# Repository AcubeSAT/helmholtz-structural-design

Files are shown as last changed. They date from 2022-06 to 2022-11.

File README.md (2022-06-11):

## **Hello, Helmholtz enthusiasts!**

This readme is for people who don't want to or don't know how to use a 3D CAD software.
*Click each of the following links to be redirected to a page where you can see the 3D design sub-assemblies and the whole assembly.*

Helmholtz assembly:
https://autode.sk/3tvBUBP

Frame:
https://autode.sk/3QcUYyy

Coil corner:
https://autode.sk/3QebGxv

All 3 coil assemblies are similar with different dimensions. Here is the middle one:
https://autode.sk/3Ha60Ay

Bracket for X and Y coils mounting:
https://autode.sk/3QhkKli

Bracket for Z coils mounting:
https://autode.sk/3NKaX5m

Helmholtz_Cage

Frame

Coil

## Have fun!

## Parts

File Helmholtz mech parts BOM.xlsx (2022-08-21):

Subassembly | No | Name | Details | Quantity | Comments
F | 1 | Vertical Beams | T-slot 20x20 aluminum profile | Length 2000mm | 4 | Procured, measured, are fine
 | 2 | Z coils supports | T-slot 20x20 aluminum profile | Length 1790mm | 4 | Procured, measured, are fine
 | 3 | ±X table supports | T-slot 20x20 aluminum profile | Length 840mm | 2 | Procured, measured, are fine
 | 4 | ±Υ table supports | T-slot 20x20 aluminum profile | Length 810mm | 2 | Procured, measured, are fine
 | 5 | X coils supports | T-slot 20x40 aluminum profile | Length 840mm | 4 | Procured, measured, are fine
 | 6 | Y coils supports | T-slot 20x40 aluminum profile | Length 810mm | 4 | Procured, measured, are fine
 | 7 | Testing table | Aluminum sheet 2x840x810mm | 1 | Not procured yet
 | 8 | Double profile brackets | 20x40 aluminum brackets (4 bolt holes) | 16 | Procured, assemblable
 | 9 | Square profile brackets | 20x20 aluminum brackets (2 bolt holes) | 16 | Procured, assemblable
 | 10 | M5 stainless steel bolts |  | 128 | Procured galvanized steel ones for assembly, reordered correct ones) dimension concern for length
 | 11 | M5 stainless steel nuts |  | 128 | Procured galvanized steel ones for assembly, reordered correct ones)
 | 12 | Z coils brackets |  | 8 | Not finished printing yet (need a small alteration)
 | 13 | X-Y coils brackets |  | 16 | Not finished printing yet
X Y Z | 14 | Corner ground parts | thickness 3mm | 24 | Procured, assembled
 | 15 | Corner side parts | thickness 2mm | 48 | Procured, assembled
Z | 16 | Z coil channels | Aluminum U-profile 20x50 length 1650mm | 8 | Procured, assembled
Y | 17 | Y coil channels | Aluminum U-profile 20x50 length 1600mm | 8 | Procured, assembled
X | 18 | X coil channels | Aluminum U-profile 20x50 length 1550mm | 8 | Procured, assembled
X Y Z | 19 | Rivets | Aluminum 4mm diameter | 192 | Procured, assembled

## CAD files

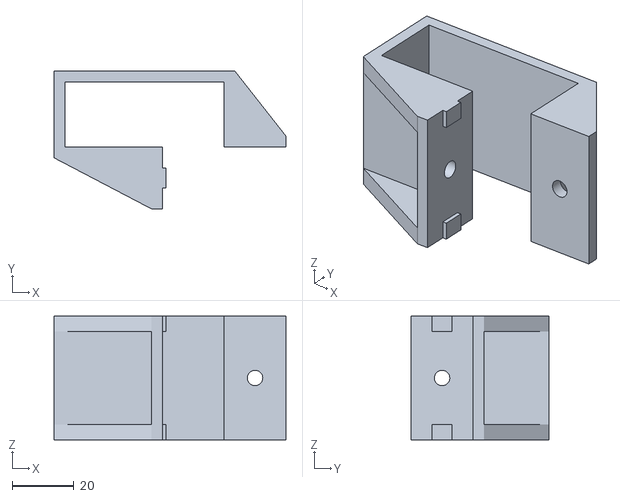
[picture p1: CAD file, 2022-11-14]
Helmholtz X-Y bracket (NEW 14-11-2022) (PITSOS - CHATZIARGIRIOU).STL
75.0 x 44.5 x 40.0

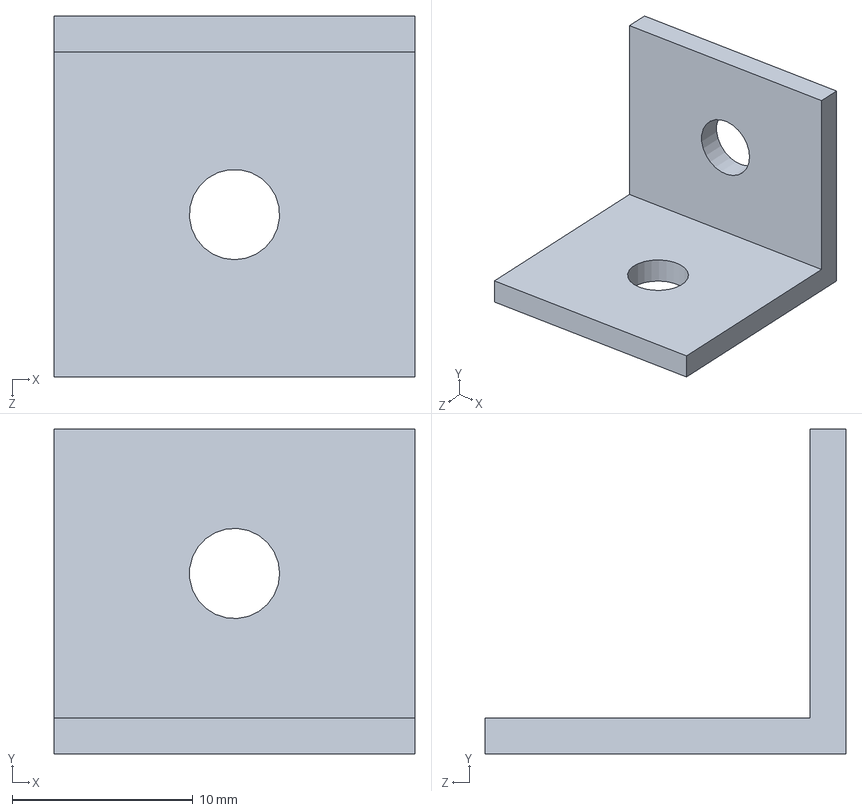
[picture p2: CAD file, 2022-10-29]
Support bracket (simple).SLDPRT
20.0 x 18.0 x 20.0 mm

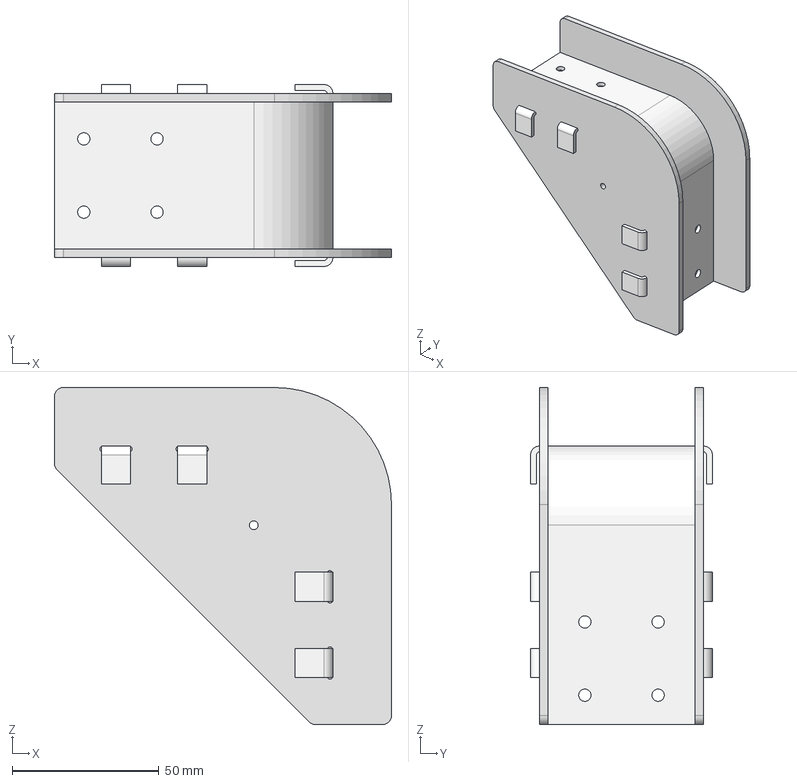
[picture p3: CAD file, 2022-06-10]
Corner v2.stp
115.0 x 62.0 x 115.0 mm
Corner side v2 x 2
Corner ground v2

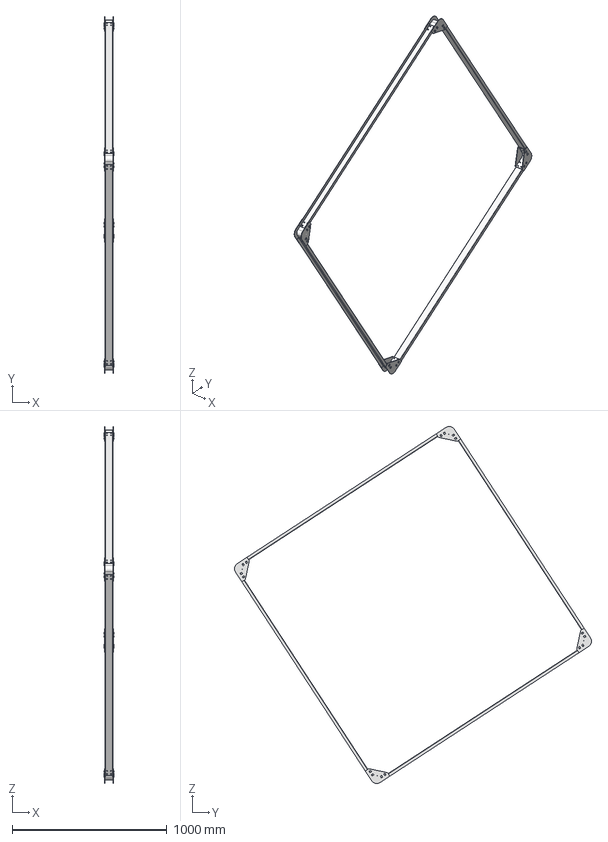
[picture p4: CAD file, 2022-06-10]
Inner coil v2.stp
62.0 x 2308.0 x 2308.0 mm
Inner channel x 4
Corner side v2 x 8
Corner ground v2 x 4
rivets x 32

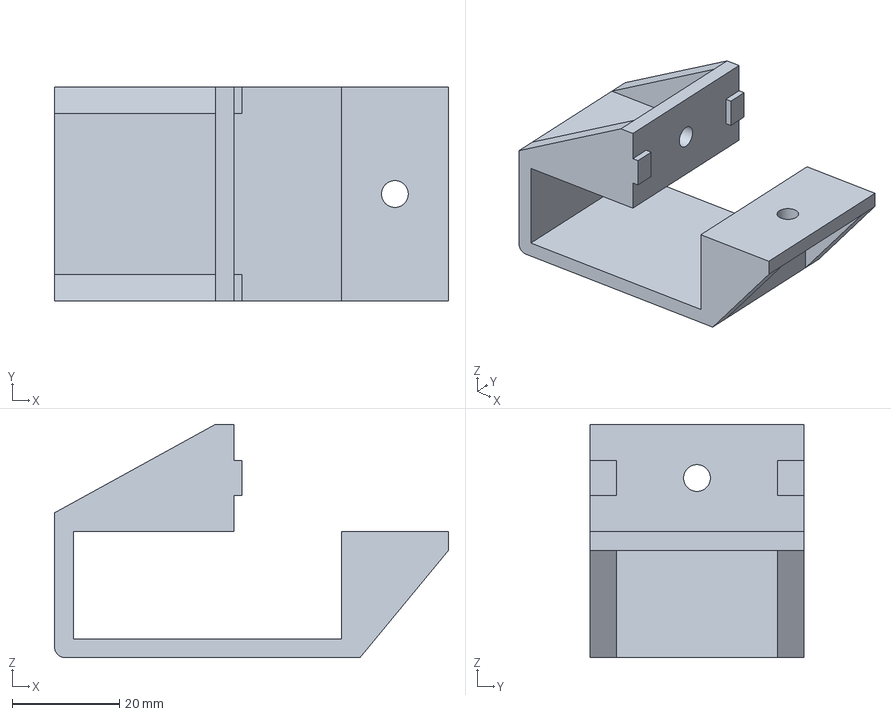
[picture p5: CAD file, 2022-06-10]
X-Y bracket.stp
73.5 x 40.0 x 43.5 mm

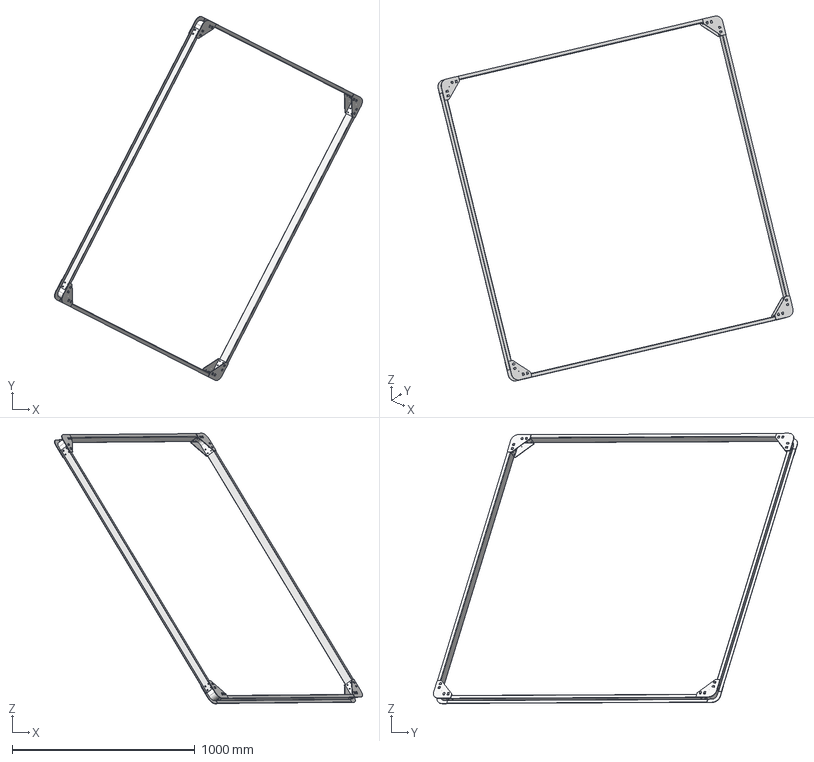
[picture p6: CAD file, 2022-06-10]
Middle coil v2.stp
1684.5 x 1991.8 x 1479.6 mm
Corner side v2 x 8
Corner ground v2 x 4
Middle channel x 4
rivets x 32

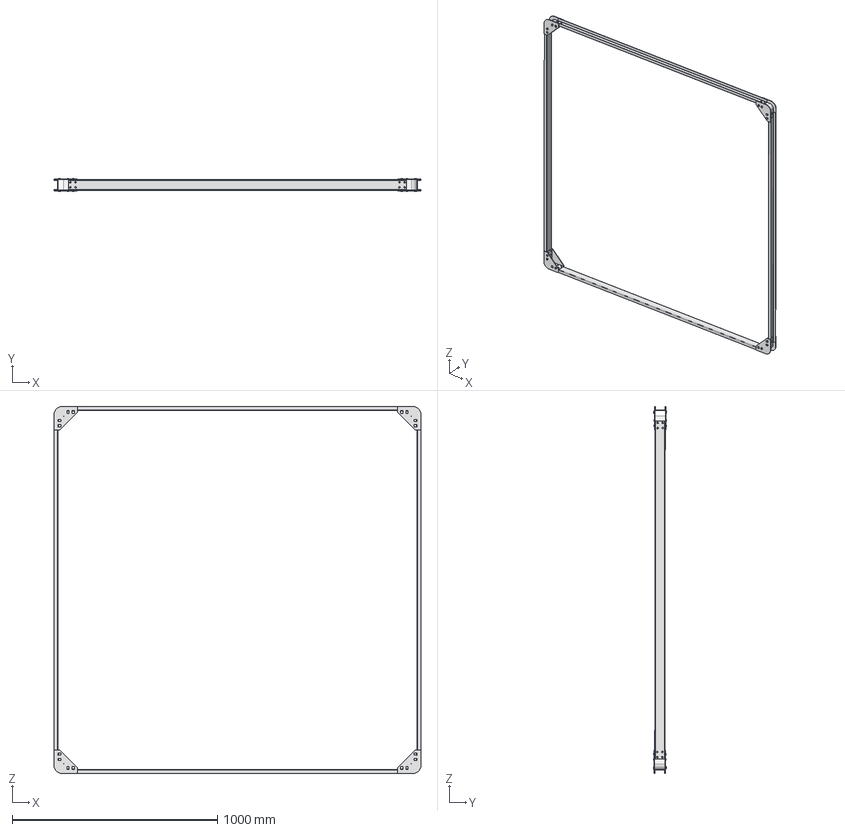
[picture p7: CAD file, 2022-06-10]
Outer coil v2.stp
1790.0 x 63.5 x 1790.0 mm
Corner side v2 x 8
Corner ground v2 x 4
Outer channel x 4
rivets x 32

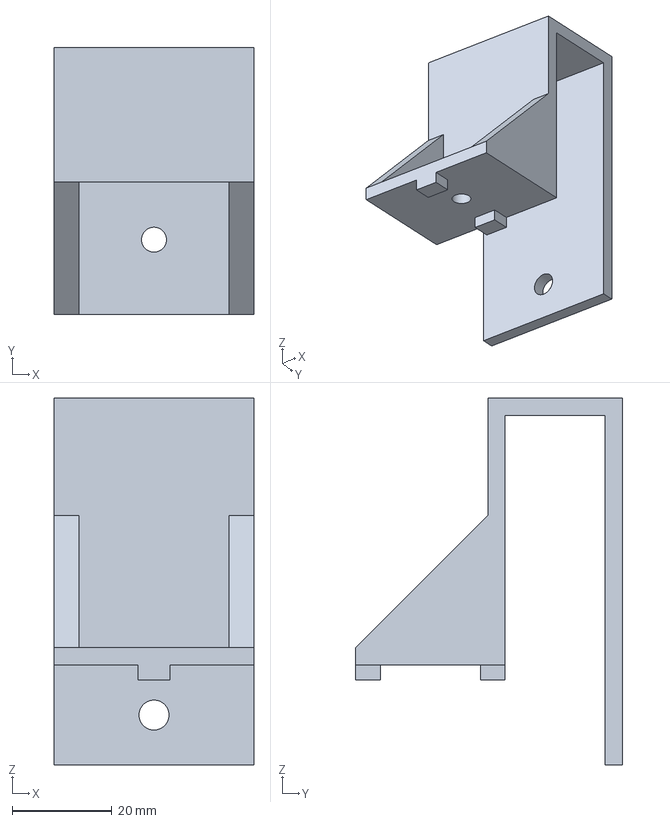
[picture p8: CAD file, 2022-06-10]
Z bracket.stp
40.0 x 53.5 x 73.5 mm

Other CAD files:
Mechanical drawings/Corner side v2.dwg
Mechanical drawings/Corner ground v2.dwg
Support bracket (simple).STL

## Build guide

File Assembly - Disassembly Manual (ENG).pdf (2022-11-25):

## BILL OF MATERIALS

1. 128 Μ5 stainless steel bolts
2. 128 Μ5 stainless steel nuts
3. 4 Vertical beams (T-slot 20x20 aluminum profile - Length 2000mm)
4. 4 Z coils beams (T-slot 20x20 aluminum profile - Length 1790mm)
5. 4 X coils beams (T-slot 20x40 aluminum profile - Length 840mm)
6. 4 Y coils beams (T-slot 20x40 aluminum profile - Length 810mm)
7. 1 Testing table (Aluminum sheet 2x840x810mm)
8. 2 ±X table beams (T-slot 20x20 aluminum profile - Length 840mm)
9. 2 ±Υ table beams (T-slot 20x20 aluminum profile - Length 810mm)
10. 16 Double profile brackets (20x40 aluminum brackets (4 bolt holes))
11. 16 Square profile brackets (20x20 aluminum brackets (2 bolt holes))
12. 8 Z coils brackets
13. 16 X-Y coils brackets
14. 2 X coils (side length 1650mm)
15. 2 Υ coils (side length 1700mm)
16. 2 Z coils (side length 1750mm)
17. 16 support brackets

For the assembler’s convenience, the following parts shall be renamed:
Item number, from BoM | Initial name, from BoM | Final name, referred as in document
3 | Vertical beams (T-slot 20x20 aluminum profile -Length 2000mm) | XL
4 | Z coils beams (T-slot 20x20 aluminum profile -Length 1790mm) | L
5 | X coils beams (T-slot 20x40 aluminum profile -Length 840mm) | x2/84
6 | Y coils beams (T-slot 20x40 aluminum profile -Length 810mm) | x2/81
8 | ±X table beams (T-slot 20x20 aluminum profile - Length 840mm) | TBL X
9 | ±Υ table beams (T-slot 20x20 aluminum profile - Length 810mm) | TBL Y
10 | Double profile brackets (20x40 aluminum brackets (4 bolt holes)) | Double brackets
11 | Square profile brackets (20x20 aluminum brackets (2 bolt holes)) | Single brackets

## PRELIMINARY WORK

Brackets preparation
We take a screw, pass it through a hole of our choice from a double bracket and screw a nut on the other side, making sure that the flat surface of the nut faces the double bracket. We repeat this procedure for all the double brackets, and work similarly for the single brackets. It is important that half of the double brackets have the screw in the left hole, and the other half have it in the right, like they are projections on a mirror.

Preparation of x2/84 and x2/81 supports
We assemble all the x2/84 and x2/81 supports. On the 40mm wide surface (big surface), and channel of our choice, we insert a double bracket with the blank back facing outwards and align the back of the double bracket with the edge of the support, then tighten the screw. We repeat the process on the other side of the support. CAUTION!!! At this point, the screws from the two double brackets should be in the same channel of the big surface of the x2/84 and x2/81 supports.

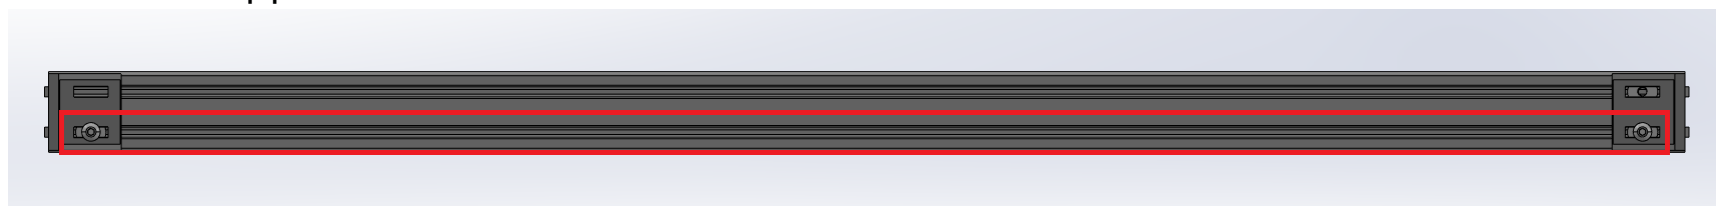
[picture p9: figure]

Preparation of the TBL X and TBL Y supports
We assemble all of the TBL X and TBL Y supports. Using the single brackets, we work similarly to the preparation of the x2/84 and x2/81 supports.

Preparation of the L supports
We assemble all the L supports. At a distance equal to 47.1cm from each side, we mark the point. For the input of a single bracket, we insert it in the channel with the back with the empty hole facing outside of the L support (at 90 degrees). We align the single bracket's flat surface, which is facing towards the side it was inserted from, with the 47,1cm mark and tighten the screw. We repeat this procedure for the other side of this L support. We repeat this procedure for all the L supoorts. CAUTION!!! The surface with the empty hole of all the single brackets must be facing the same way.

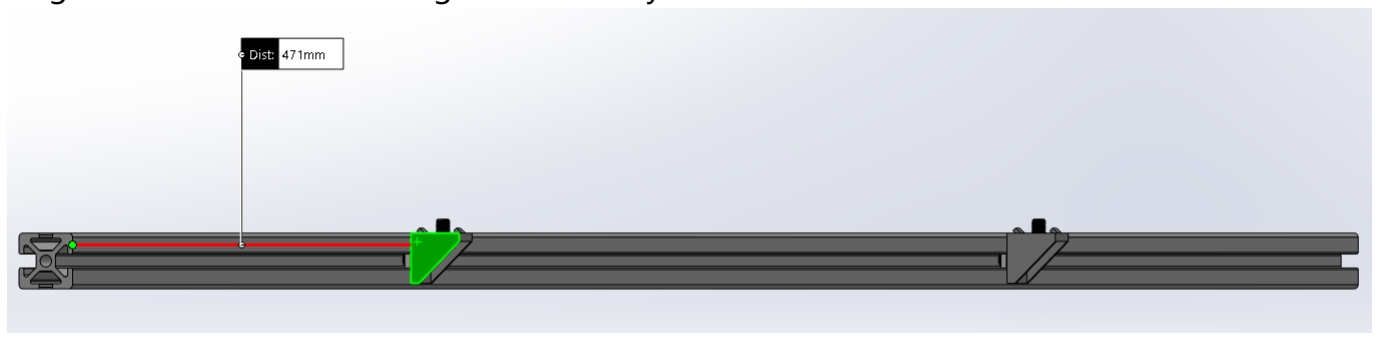
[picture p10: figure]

Figure 1. Single brackets distance and placing
At this point, the 4 L supports should have 8 single brackets mounted on them, in total, which will all be in the same channel, and the empty hole of all the single brackets will be facing the same way.

## ASSEMBLY

COALESCENCE OF THE 4 XL BEAMS
For the assembler's convenience, the bottom of the XL beams will be called the (-) side, whereas the top will be called the (+) side.

We take 2 XL beams and at a distance of 26cm from the bottom (-), we mark the spot. We take one x2/81 support and insert it in the channel of an XL beam with its blank side facing the top (+) of the cage, while the side which bears the double bracket faces the bottom (-). We align the blank surface with the 26cm mark, and tighten the screw. We repeat this process for the other XL beam. Finally, we repeat all the above steps with the other 2 XL beams and 1 x2/81 support. CAUTION!!! The protruding part of the x2/81 support MUST be towards the outside area of the cage.

At this point, we have joined together the 4 XL beams in pairs of 2.

Next, at a distance of 28.7cm from the bottom (-) of the XL beams, we mark the spot. Using one of the two pairs of XL beams, we insert a x2/84 bracket into the channel of an XL bracket with the blank surface facing the top (+) and the side with the double brackets facing the base (-). Align the blank surface with the 28.7cm mark, and tighten the screws to stabilize the support. We are now able to join the 2 pairs by inserting the other end of this x2/84 support into the channel of the other XL pair. Finally, we insert another x2/84 from the other side and work in a similar way to close the loop. CAUTION!!! At this point the 4 XL brackets should be joined together, and the side of x2/81 and x2/84 that protrudes from the frame should be OUTSIDE the cage.

At this point, the cage should look like this.

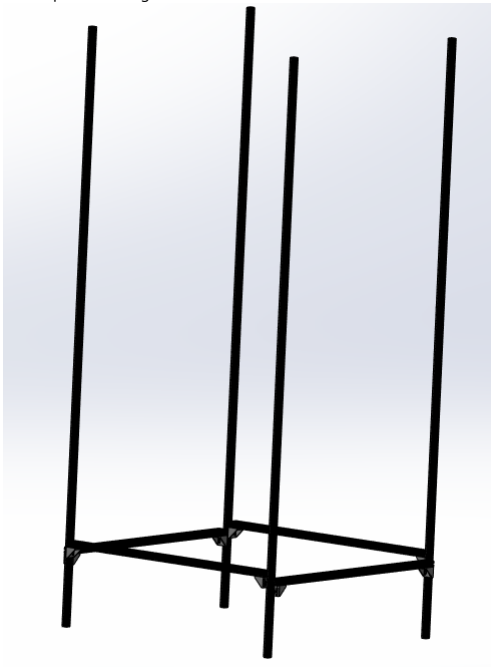
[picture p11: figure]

Figure 2. Coalescence of the XL supports

LOWER Z SUPPORTS PLACEMENT
At a distance equal to 60.9cm from the base (-) we mark the spot. The L supports MUST be inserted on the same sides as the x2/81 supports. The L supports MUST be facing the inside area of the cage. We align the blank surface with the 60.9cm mark, facing the top (+), and tighen the screw.

At this point, the cage should look like this.

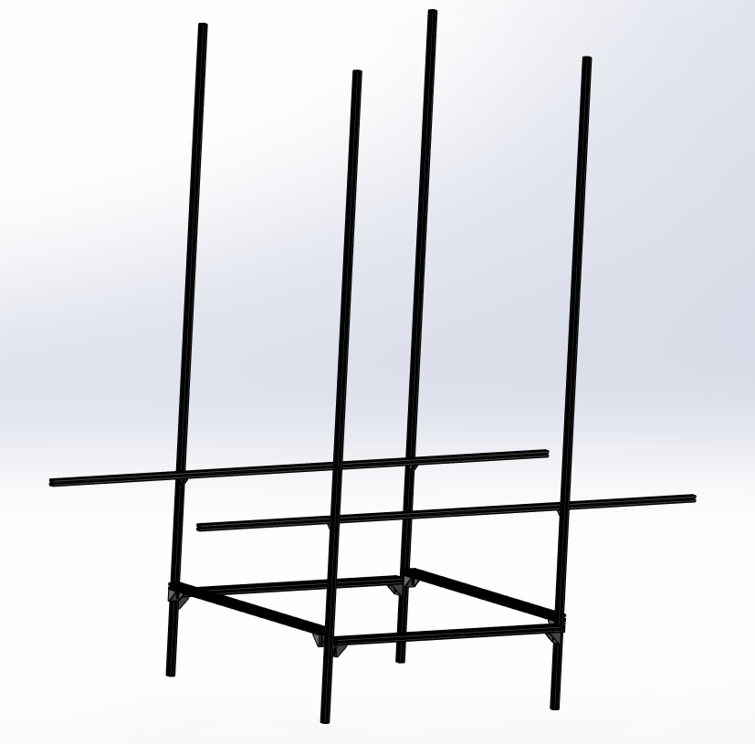
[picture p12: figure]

Figure 3. Lower Z supports
TABLE PLACEMENT
At a distance equal to 113cm from the base (-) we mark the spot.
To mount the TBL X supports, we insert them from the same sides as the x2/84 supports. To install the first TBL X, insert the bracket with the single bracket side facing the base (-). Align the blank surface of the TBL X with the 113cm mark, and tighten the screw. Repeat the procedure for the other TBL X support. In a similar way, we insert the TBL Y brackets from the sides of the x2/81 brackets, and repeat the procedure.

At this point, we have the 4 table brackets TBL X and TBL Y with their blank surface aligned with the 113cm mark, and with the single bracket facing the base (-). Also, the TBL X are parallel to the x2/84, while the TBL Y are parallel to the x2/81.

We place the table on top of its supports, with the longer side (840mm) on the TBL X supports and the shorter side (810mm) on the TBL Y supports.

At this point, the cage should look like this.

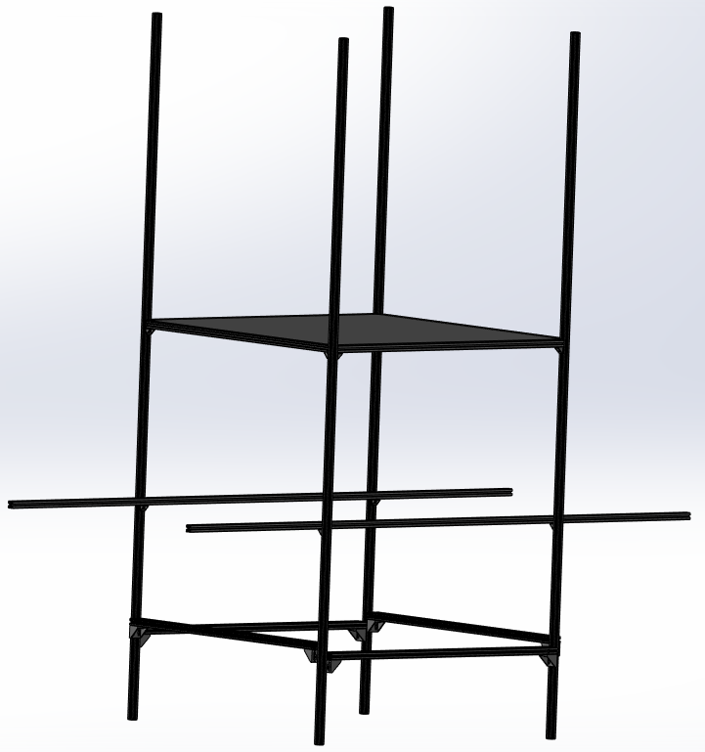
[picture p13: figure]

Figure 4. Table and its supports

UPPER Ζ SUPPORTS PLACEMENT
At a distance equal to 156.1cm from the base (-) we mark the spot. The L supports MUST be inserted on the same sides as the x2/81 and TBL Y supports. The L supports MUST be facing the inside area of the cage. We align the blank surface with the 156.1cm mark, facing the top (+), and tighen the screw.

At this point we have placed the 4 L supports, facing towards the inside are of the cage, and parallel to the x2/81 and TBL Y supports.

At this point, the cage should look like this.

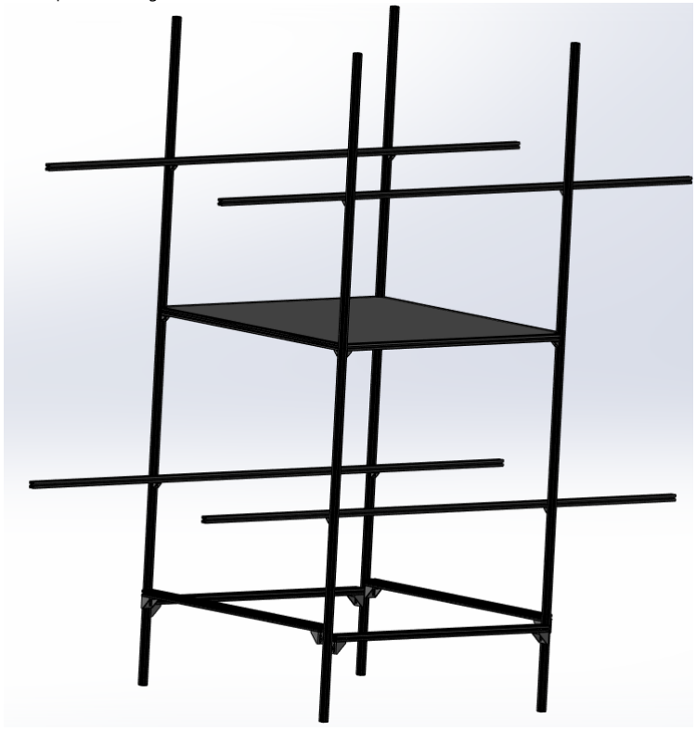
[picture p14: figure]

Figure 5. Upper Z supports

TOP SUPPORTS PLACEMENT
At a distance of 2cm and 4.35cm from the top (+), we mark the spot.

For the placement of the final 2 x2/81 supports, we insert them from the top (+) of the sides that have the other 2 x2/81 and TBL Y supports mounted. We insert them with the brackets facing towards the base (-), align the blank surface with the 2cm mark, and tighten the screws.

Similarly, we mount the final 2 x2/84 supports to the top (+) of the sides that have the other 2 x2/84 and TBL X supports. We align the blank surface with the 4.35cm mark, and tighten the bolts.

At this point, we have set up the main frame infrastructure, alongside all the internal supports. The cage should look like this.

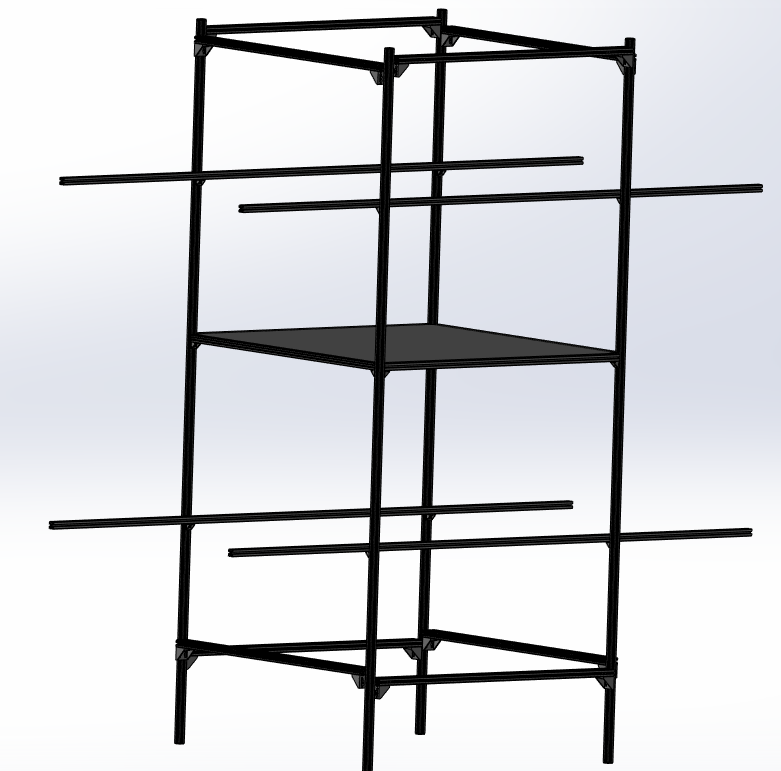
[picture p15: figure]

Figure 6. Top supports

COILS PLACEMENT
The first coils to be mounted are the X coils (side length 165cm) atop the x2/84 supports. Next, the Y coils are placed (side length 170cm) atop the x2/81 supports. During the Y coils' installation, we mount them outside of the X coils.

Finally, we place the Z coils (side length 175cm) outside of the other 2, and mount them atop the L supports.

At this point, the cage should look like this.

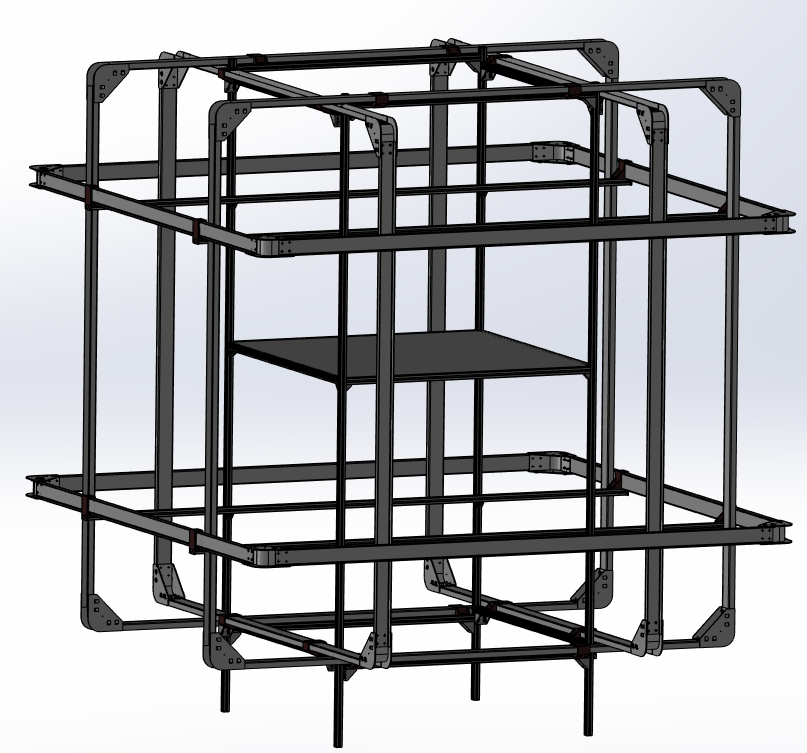
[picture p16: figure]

Figure 7. Assembled Helmholtz cage, with frame and coils

## SUPPORT BRACKETS

In order ot further improve the overall stability of the assembly, 3D printed brackets are being utilized.
There are 3 types of brackets:
- X-Y brackets for the X-Y coils
- Z brackets for the Z coils
- Support brackets for the x2/81 and x2/84 beams

The X-Y brackets keep the X and Y coils in place atop the x2/81 and x2/84 beams. There is no fixed position for them to be screwed. It's up to the assembler.

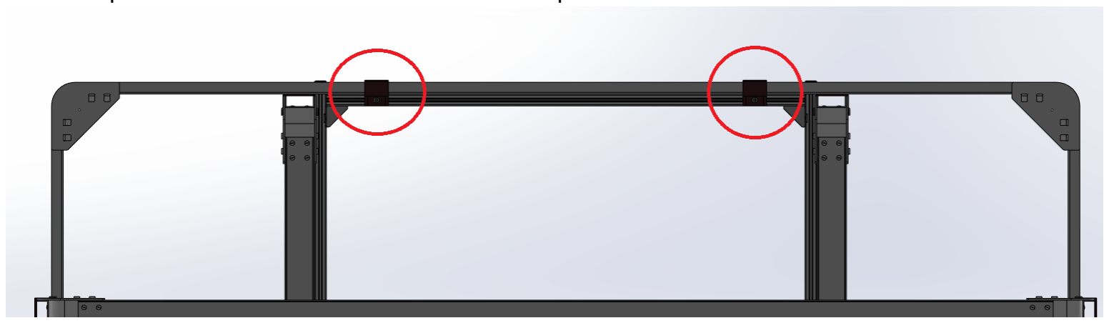
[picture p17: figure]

The Z brackets keep the Z coils in place at the edges of the L beams.
If the inside of the beam is threaded, an additional screw may be used to further stabilize the assembly.

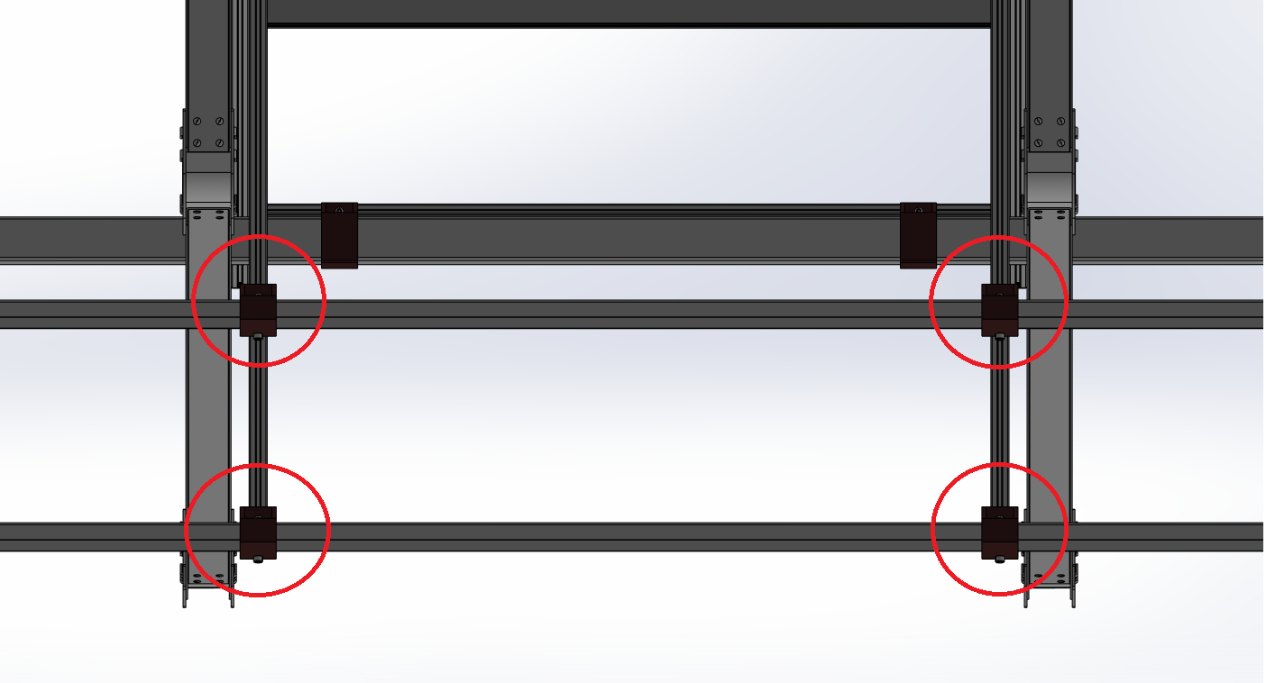
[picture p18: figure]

The support brackets further stabilize the x2/81 and x2/84 beams, keeping them from rotating due to the coils' weight.

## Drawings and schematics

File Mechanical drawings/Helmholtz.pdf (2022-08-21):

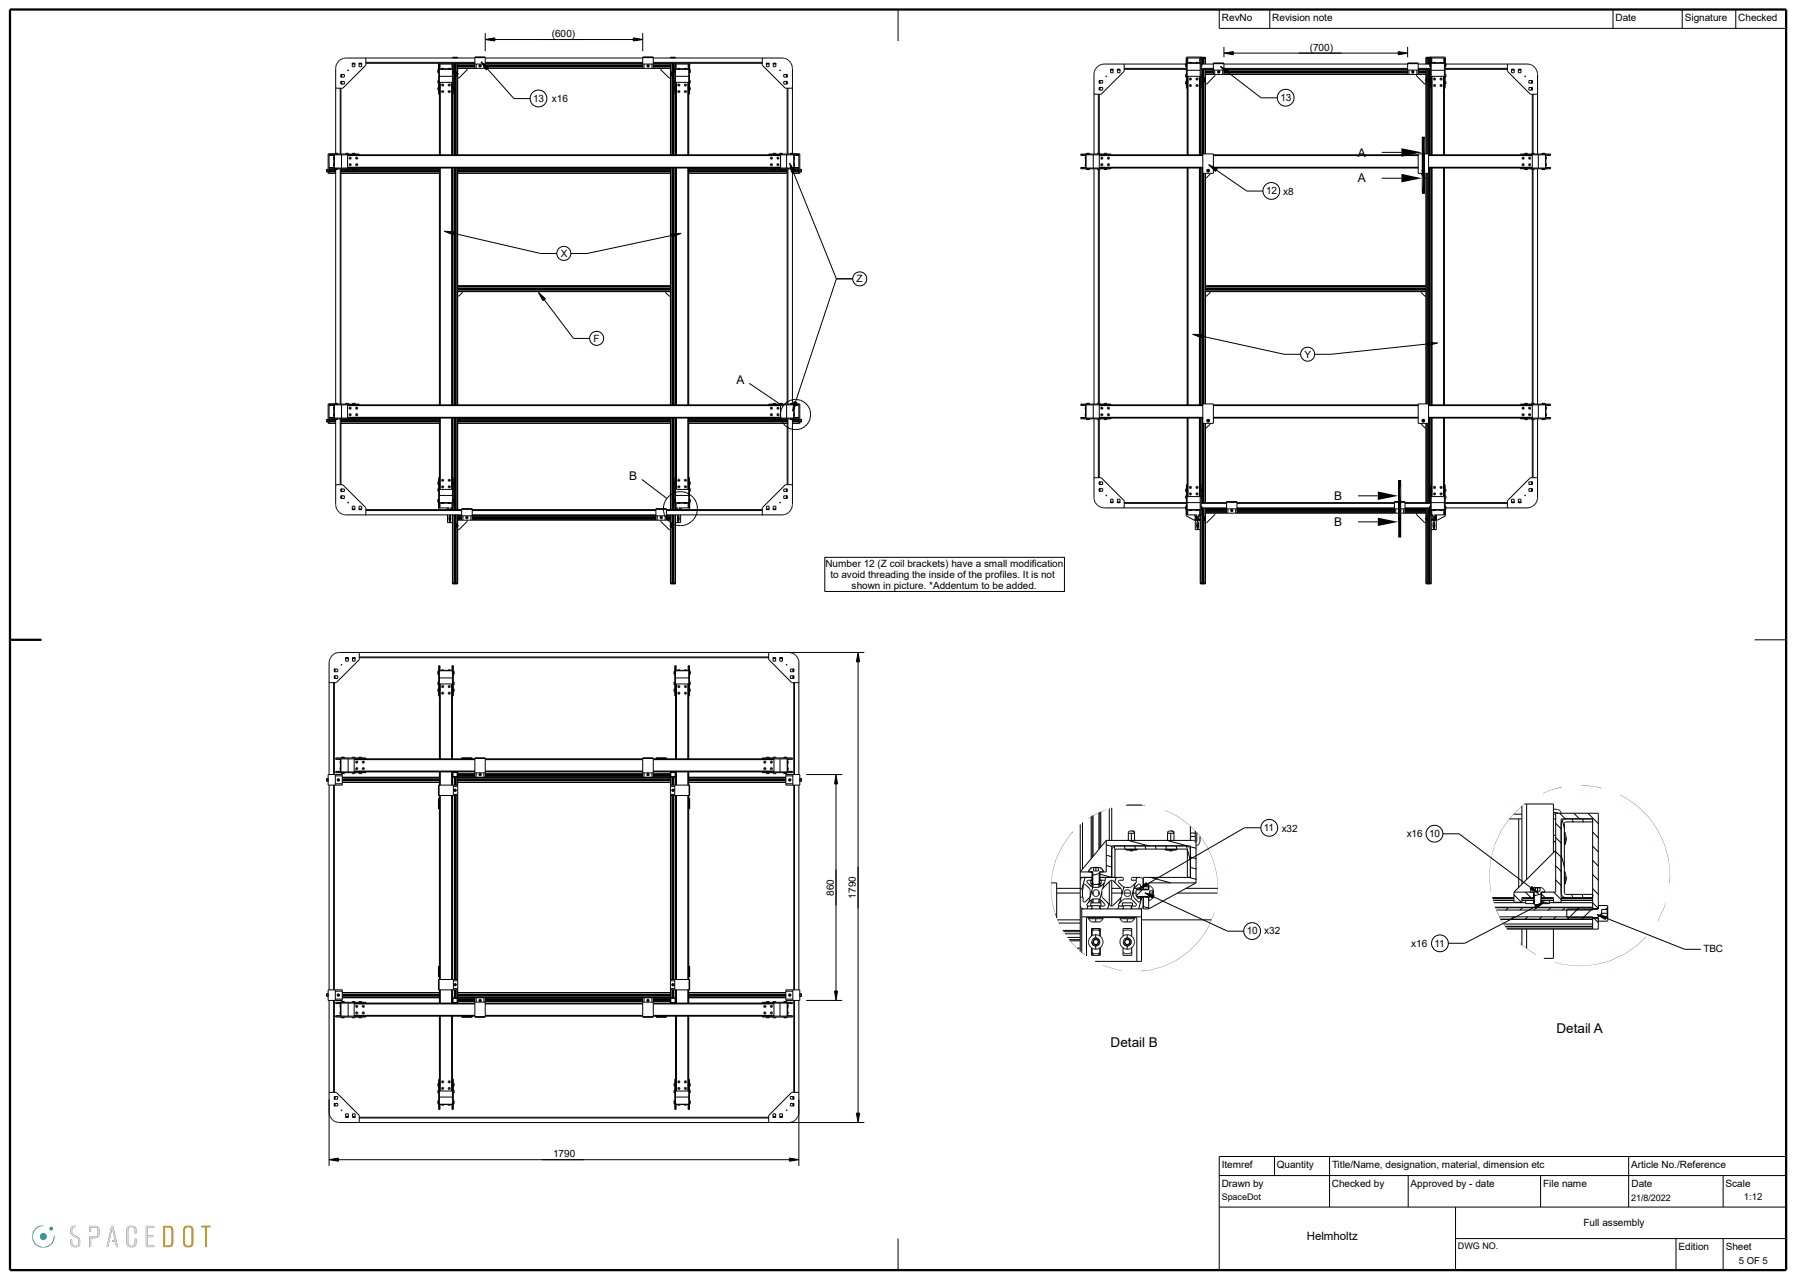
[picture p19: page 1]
Detail A; TBC; Detail B; Checked by; DWG NO. Drawn by; Approved by - date; Scale; Edition; Sheet; Itemref; RevNo; Title/Name, designation, material, dimension etc; Article No./Reference; Checked; File name; Date; Signature; Quantity; Revision note; SpaceDot; Helmholtz; Full assembly

Number 12 (Z coil brackets) have a small modification
to avoid threading the inside of the profiles. It is not
shown in picture. *Addentum to be added.

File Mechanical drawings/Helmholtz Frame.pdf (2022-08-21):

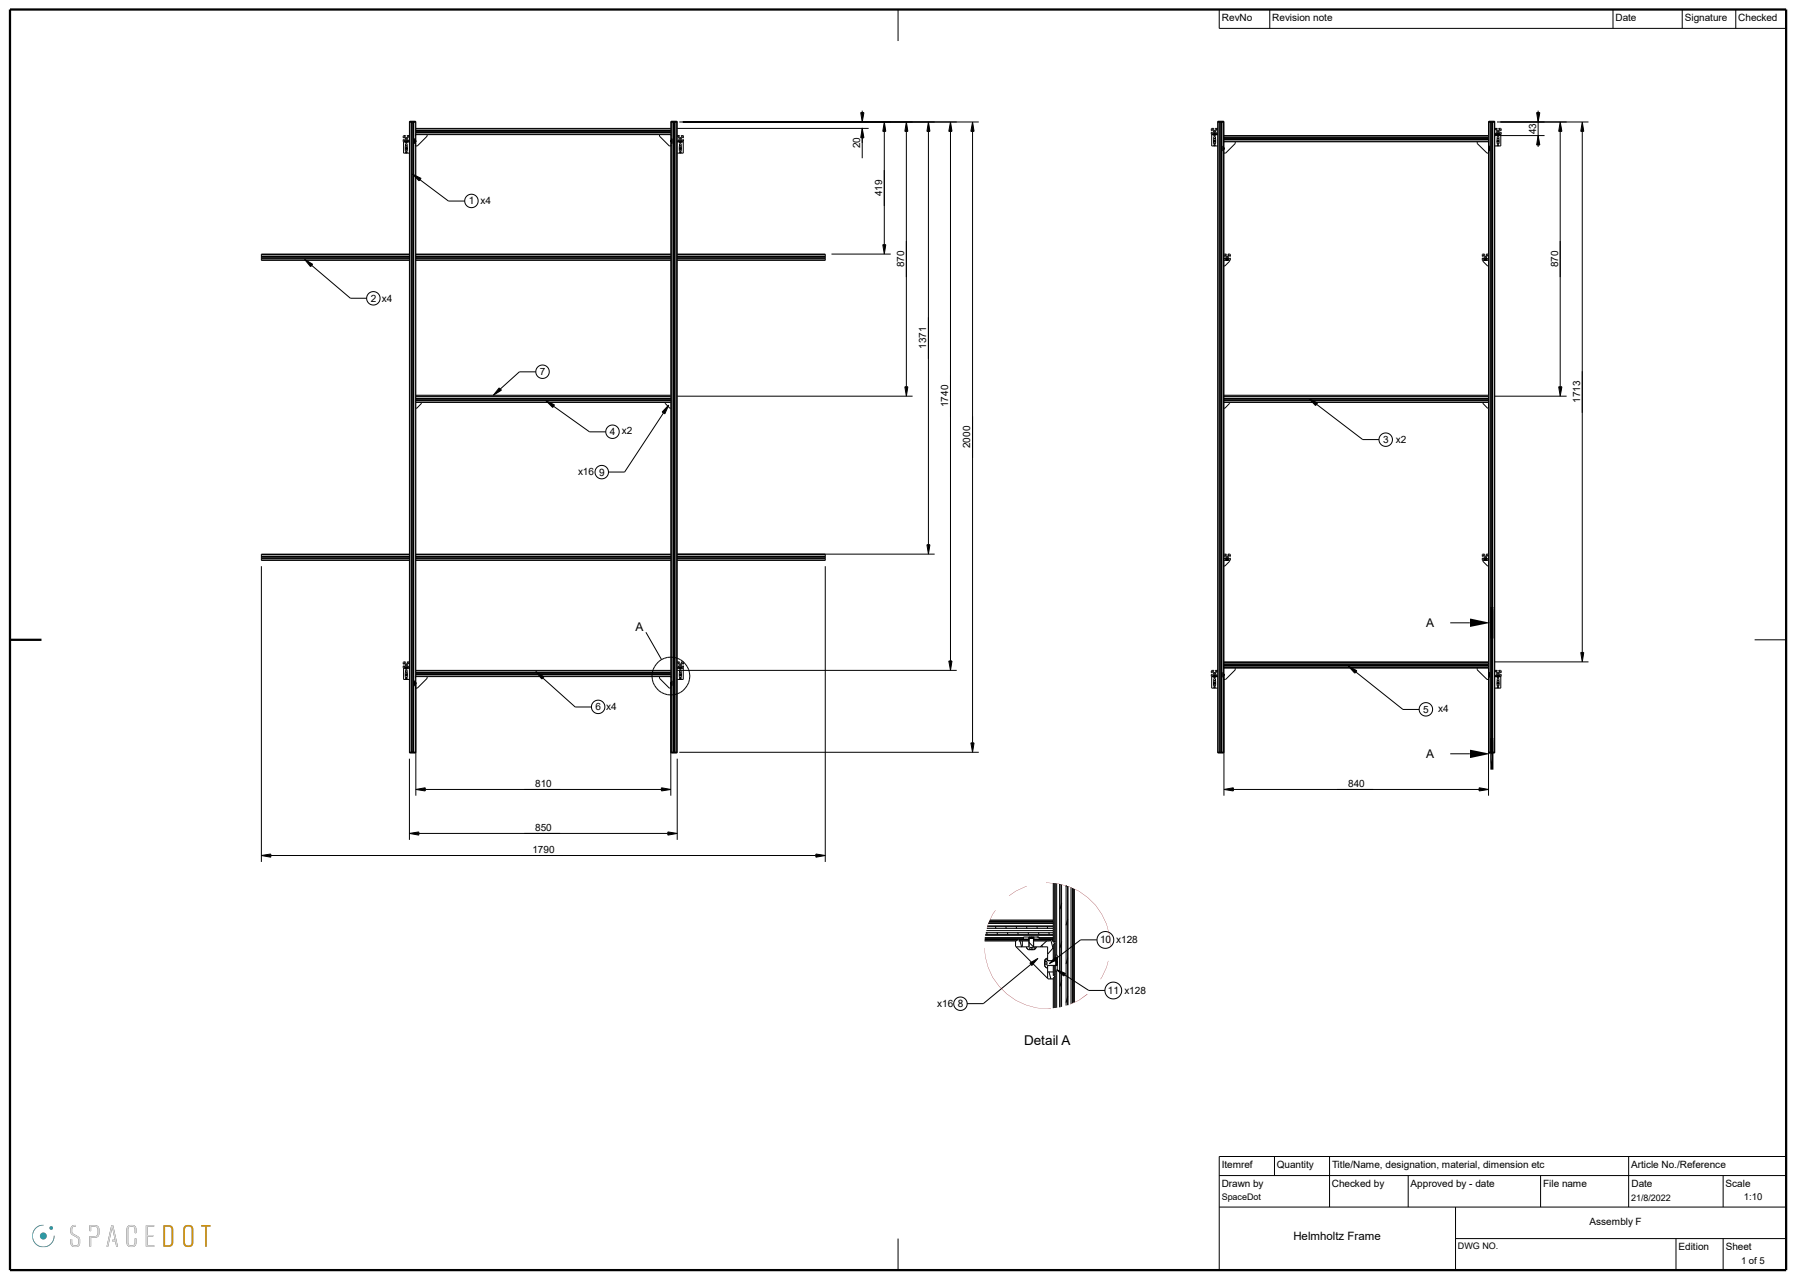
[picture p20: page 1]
Detail A; RevNo; Edition; Scale; Date; Sheet; Signature; Drawn by; Itemref; Quantity; File name; Revision note; Checked; SpaceDot; Helmholtz Frame; Assembly F

Title/Name, designation, material, dimension etc
Checked by

Article No./Reference

Approved by - date

Date DWG NO.

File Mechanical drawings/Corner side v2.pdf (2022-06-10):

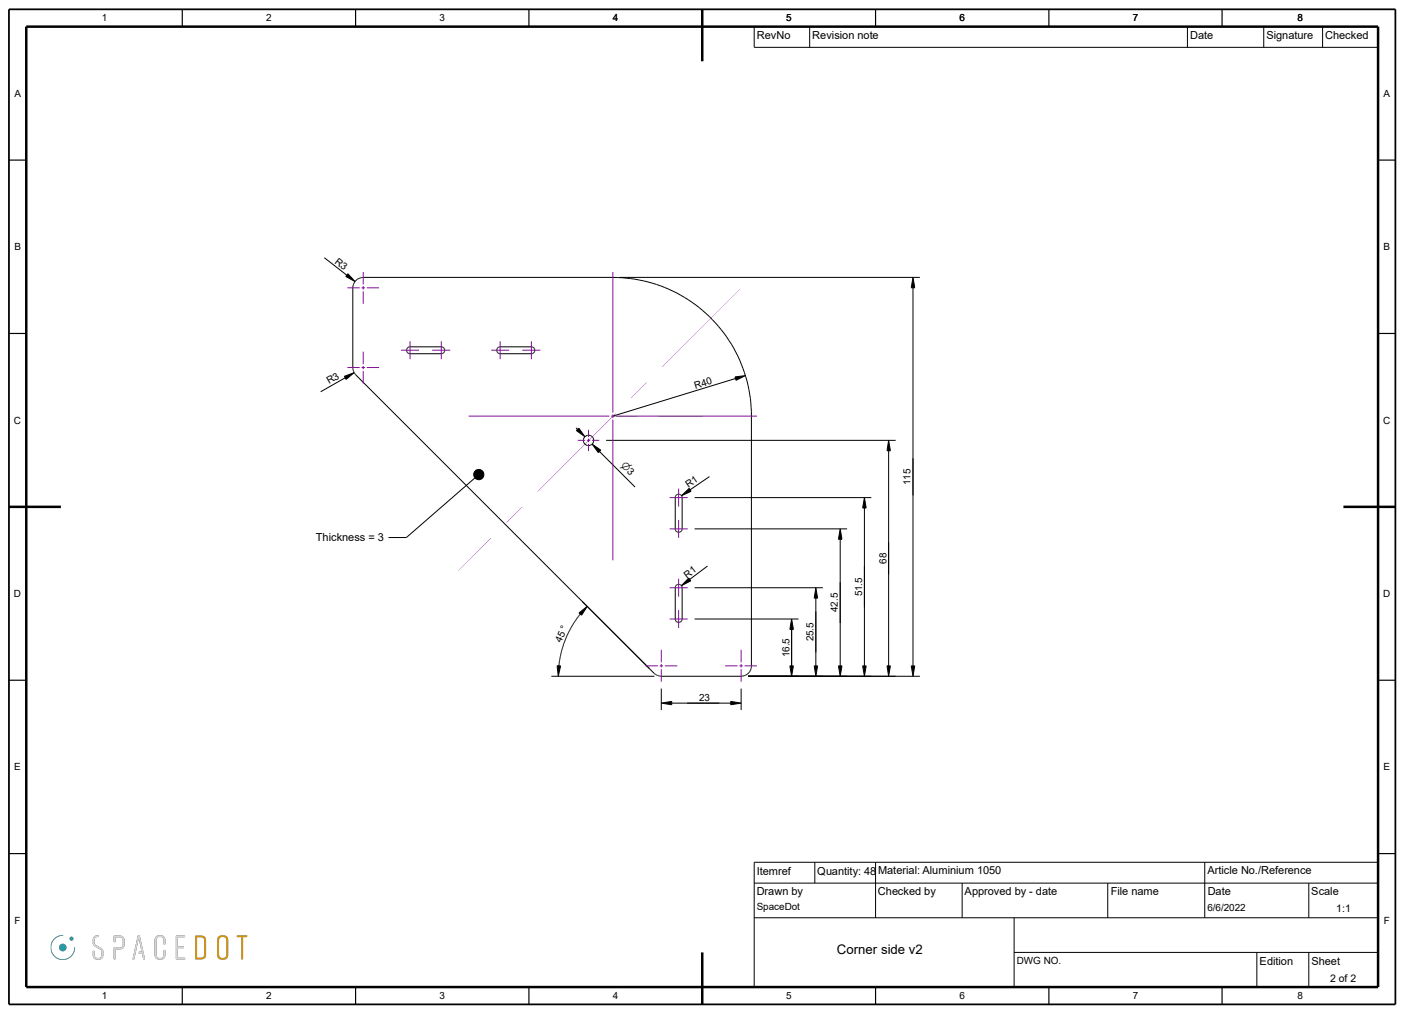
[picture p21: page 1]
Thickness = 3

RevNo | Revision note | Date | Signature | Checked

Itemref | Quantity: 48 Material: Aluminium 1050 | | Article No./Reference
Drawn by SpaceDot | Checked by | Approved by - date | File name | Date 6/6/2022 | Scale 1:1

Corner side v2

DWG NO. | Edition | Sheet 2 of 2

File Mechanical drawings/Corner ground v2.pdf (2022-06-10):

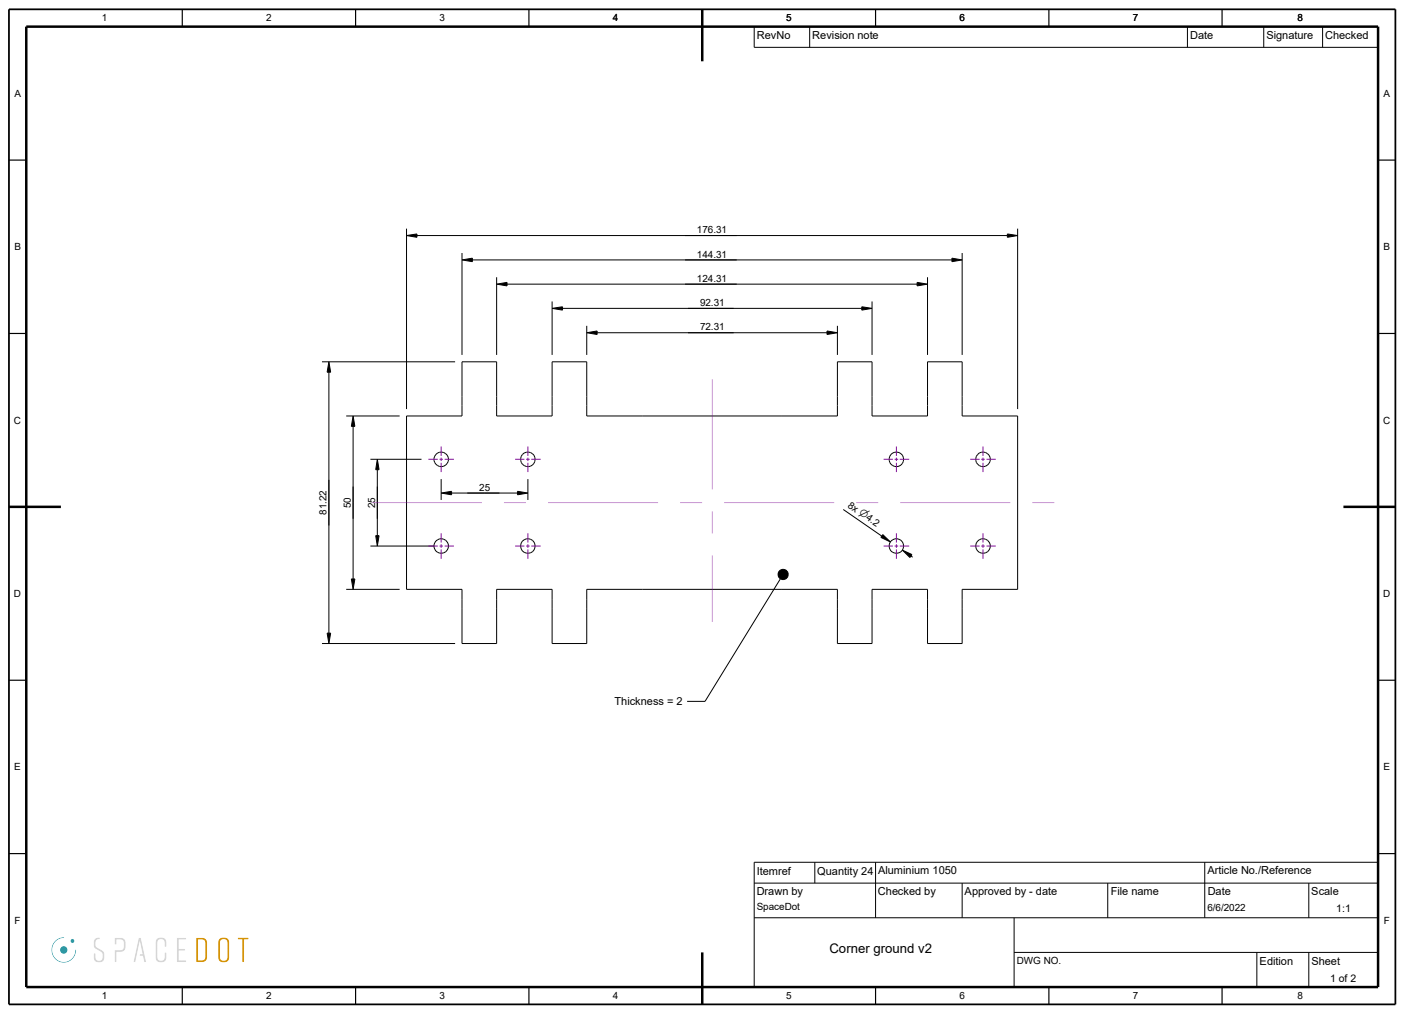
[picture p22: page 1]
Thickness = 2

RevNo | Revision note | Date | Signature | Checked

Itemref | Quantity 24 | Aluminium 1050 | Article No./Reference
Drawn by SpaceDot | Checked by | Approved by - date | File name | Date 6/6/2022 | Scale 1:1

Corner ground v2

DWG NO. | Edition | Sheet 1 of 2

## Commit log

2022-03-28 Upload New File
    [Helmholtz_cage.stp]
2022-03-28 Upload first coil CADs version
    [Center coil assembly.stp, Center coil channel.stp, Coil corner side piece.stp, Corner piece assembly.stp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]
2022-04-11 Change Cads to improved version
    Final (I hope) version of 3d cads.
    [40x40 (bolted parallel).stp, 40x40 corner.stp, 80x80 corner (bolted).stp, 80x80 corner.stp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]
2022-04-23 Change design to fit 50x20x2 U-profile
    [Bracket horizontal coils (bolted).stp, Bracket horizontal coils.stp, Bracket vertical coils (bolted).stp, Bracket vertical coils.stp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]
2022-05-02 Fix small mistake in dimensions
    [Helmholtz.stp]
2022-05-17 Create mechanical drawings
    Mechanical drawings of the aluminum sheet corners were created for laser cutting and bending. Some minor dimension changes for the corners.
    [Corner Side.dwg, Corner ground.dwg, Corner ground.stp, Corner side.stp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]
2022-05-29 Change 40 series to 20 series
    Changed the design to include 20x20 mm profiles
    [20x20 bracket.stp, 40x40 (bolted parallel).stp, 40x40 bracket.stp, 40x40 corner.stp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]
2022-06-10 Upload Final Visuals
    This version has the final visualization of the helmholtz. Check the readme to see the respective links for autodesk viewer render of each of the step files.
    [20x20 bracket.stp, 40x40 bracket.stp, Corner Side.dwg, Corner ground v2.dwg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]
2022-08-21 Upload frame assembly drawing
2022-08-21 Upload Helmholtz assembly drawing
2022-08-21 Upload BOM for manual
    This BOM has part IDs for drawing reference, number of parts and info on them
    [Helmholtz mech parts BOM.xlsx]
2022-10-29 Print 16 Support Brackets on Monday 31-10
    [Support bracket (simple).SLDPRT]
2022-10-31 Print suppport brackets for cage
    [Support bracket (simple).STL]
2022-10-31 print simple bracket gcode
2022-11-09 Develop latex document for the assembly guide
2022-11-14 Print new Brackets
    [Helmholtz X-Y bracket (NEW 14-11-2022) (PITSOS - CHATZIARGIRIOU).STL]
2022-11-25 Convert the Assembly/Disassembly guide to LaTeX
